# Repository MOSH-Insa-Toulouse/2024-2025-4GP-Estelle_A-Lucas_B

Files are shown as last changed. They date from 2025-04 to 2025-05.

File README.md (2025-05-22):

# 2024-2025-4GP-Estelle AUBRY-Lucas BOURDARIE
Projet capteur 2024 - 2025 | Estelle AUBRY et Lucas BOURDARIE | 4ème année, 59ème promotion

# Table des matières

[Présentation du projet](https://github.com/MOSH-Insa-Toulouse/2024-2025-4GP-Haistelle-Lucbourd?tab=readme-ov-file#pr%C3%A9sentation-du-projet)

[I - Un capteur à base de graphite, c'est possible ?](https://github.com/MOSH-Insa-Toulouse/2024-2025-4GP-Haistelle-Lucbourd?tab=readme-ov-file#i---un-capteur-%C3%A0-base-de-graphite-cest-possible-)

[II - Simulation sous LTSpice](https://github.com/MOSH-Insa-Toulouse/2024-2025-4GP-Haistelle-Lucbourd?tab=readme-ov-file#ii---simulation-sous-ltspice)

[III - Réalisation du PCB avec KiCAD](https://github.com/MOSH-Insa-Toulouse/2024-2025-4GP-Haistelle-Lucbourd?tab=readme-ov-file#iii---r%C3%A9alisation-du-pcb-avec-kicad)

[IV - Le banc de test automatisé](https://github.com/MOSH-Insa-Toulouse/2024-2025-4GP-Haistelle-Lucbourd?tab=readme-ov-file#iv---le-banc-de-test-automatis%C3%A9)

[V - Le code Arduino pour piloter le projet](https://github.com/MOSH-Insa-Toulouse/2024-2025-4GP-Haistelle-Lucbourd/tree/main?tab=readme-ov-file#v---le-code-arduino-pour-piloter-le-projet)

[VI - L'application Android avec Mit App Inventor](https://github.com/MOSH-Insa-Toulouse/2024-2025-4GP-Haistelle-Lucbourd/tree/main?tab=readme-ov-file#vi---lapplication-android-avec-mit-app-inventor)

[VII - Résultats](https://github.com/MOSH-Insa-Toulouse/2024-2025-4GP-Haistelle-Lucbourd/tree/main?tab=readme-ov-file#vii---résultats)

# Présentation du projet 
 
<div align="justify"> Ce projet a été mené dans le cadre de l'UF  "Du capteur au banc de test" . L'objectif est de réaliser un capteur de déformation à base de graphite. Pour ce faire, il suffit simplement de déposer du crayon à papier sur un bout de feuille. La tension ou la compression du papier engendre une variation de résistance qui est proportionnelle à la déformation appliquée. Les principes physiques qui se cachent derrière ce phénomène sont expliqués <a href="https://github.com/MOSH-Insa-Toulouse/2024-2025-4GP-Haistelle-Lucbourd/blob/main/README.md#i---un-capteur-%C3%A0-base-de-graphite-cest-possible-">ici</a>. Le projet s'inscrit donc dans une démarche low-tech car le capteur nécessite peu de ressources et sa réalisation est accessible à tous !</div>

<div align="justify"> De plus, le capteur graphite réalisé sera testé de manière à comparer ses performances avec un capteur de déformation commercial. Nous souhaitons dégager les forces et les limites du capteur graphite par rapport à un capteur commercial. Finalement, nous établirons une conclusion quant à la possible industrialisation de ce type de capteur.</div>

<br>

<div style='display:flex' align="center">
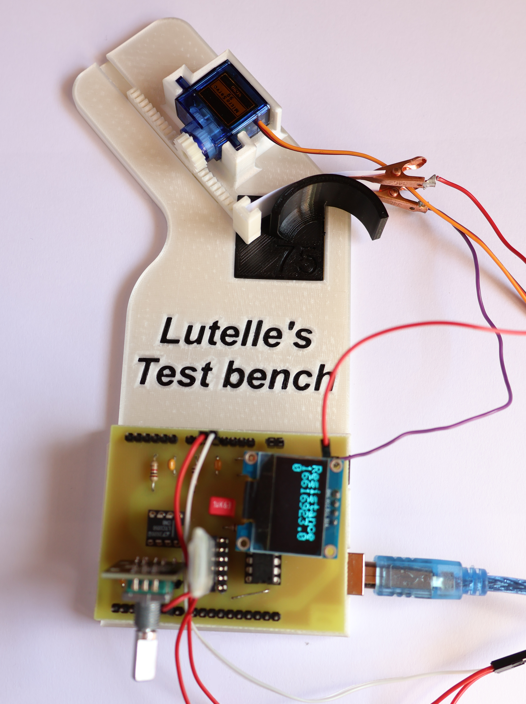
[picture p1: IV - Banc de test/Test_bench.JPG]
   
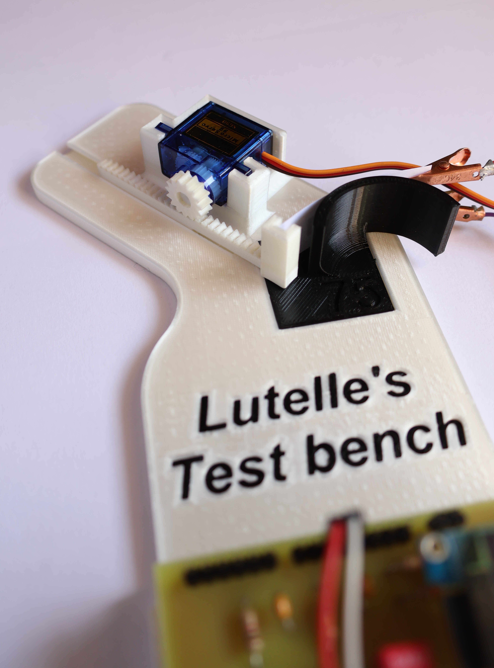
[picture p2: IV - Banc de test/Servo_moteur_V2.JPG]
   
 <p><em>Figure 1 : Banc de test complet </em></p>
</div>

<div style='display:flex' align="center">
   
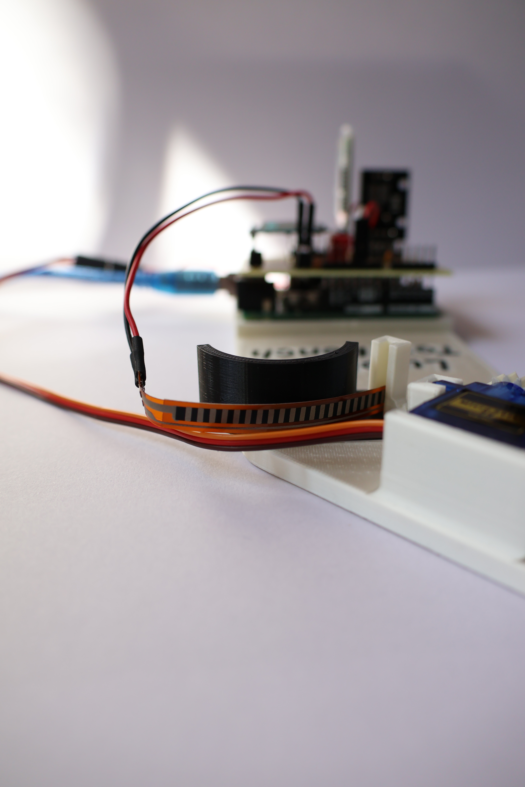
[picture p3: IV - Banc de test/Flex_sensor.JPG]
   
 <p><em>Figure 2 : Mise en place des deux types de capteurs disponibles </em></p>
</div>

 ## Livrables
À la fin de ce projet, plusieurs livrables sont attendus:
- Un **PCB** sur lequel seront connectés tous les éléments cités dans la partie [Matériel utilisé](https://github.com/MOSH-Insa-Toulouse/2024-2025-4GP-Haistelle-Lucbourd/blob/main/README.md#mat%C3%A9riel-utilis%C3%A9)
- Un **banc de test** pour étudier la déformation du capteur graphite et du capteur commercial
- Un **code Arduino** qui permette de contrôler le banc de test et d'afficher les mesures de résistances
- Une <a href="https://github.com/MOSH-Insa-Toulouse/2024-2025-4GP-Haistelle-Lucbourd/blob/main/LSG180_datasheet.pdf"><strong>datasheet</strong></a> qui énonce toutes les caractéristiques du capteur graphite
- Une **application Android** (.apk) pour visualiser les relevés de mesures en direct

## Matériel utilisé 
Pour le **montage**, voici tout le matériel requis:
- Une carte Arduino UNO
- Un écran OLED (I2C) 
- Un module Bluetooth HC-05
- Un potentiomètre numérique MCP41050
- Un encodeur rotatif
- Un capteur de déformation commercial (FlexSensor) pour effectuer une comparaison
- Un <a href="https://github.com/MOSH-Insa-Toulouse/2024-2025-4GP-Haistelle-Lucbourd/blob/main/Jauge_Contrainte_A_Imprimer.pdf"><strong>capteur de déformation en papier</strong></a>
- Des crayons à papiers différents pour les tests
- Un servo moteur
- Des header de différentes tailles pour fixer les composants sur la PCB
- Une résistance de 33k

Pour réaliser **l'amplificateur transimpédance**, la liste de matériel est la suivante:
- Un amplificateur opérationnel LTC1050
- Deux condensateurs de 100nF
- Un condensateur de 1uF
- Deux résistances de 100k
- Deux résistances de 1k
- Une résistance de 10k

# I - Un capteur à base de graphite, c'est possible ?

<div align="justify">
Oui et c'est ce qu'a montré l'équipe de chercheurs Lin, CW., Zhao, Z., Kim, J. et al. dans l'article <em>Pencil Drawn Strain Gauges and Chemiresistors on Paper</em> paru en 2014. En effet, les crayons à papier sont composés de graphite et d'argile dans des proportions différentes. Par exemple, le crayon HB est constitué à 50% de graphite et à 50% d'argile. Ces différences de compositions entraînent des propriétés de conduction qui diffèrent selon le type de crayon utilisé. Lorsque l'on dépose du crayon à papier sur une feuille, les nanoparticules de graphite déposées constituent un système dit <strong>granulaire</strong>. Il s'agit d'un système dont les grains forment un réseau très désordonné au sein duquel les électrons se déplacent d'un grain à un autre par <strong>effet tunnel</strong>. L'équipe de chercheurs a donc démontré que les crayons <strong>durs</strong> comme l'HB possédaient une résistance plus importante que les crayons <strong>légers</strong> comme le 9B. Ceci s'explique par le fait que les crayons durs comme l'HB contiennent plus d'argile qu'un crayon léger qui contient plus de graphite. L'argile joue le rôle d'un isolant, plus il y en a, plus la conduction des électrons au sein du matériau est difficile. À l'inverse, les nanoparticules de graphite permettent la conduction des électrons, c'est pour cela que le crayon 9B est moins résistif que le crayon HB. 
</div>
 <br>
<div align="center">
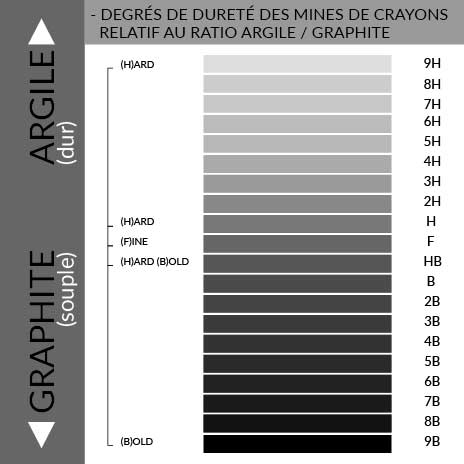
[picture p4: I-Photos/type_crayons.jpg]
  
  <p><em>Figure 3 : Les différents types de crayons: du 9B au 9H</em></p>
 <p><em>d'après le site Passage Clouté à l'adresse<a href="https://passagecloute.com/blog/post/8_comment-choisir-le-bon-crayon-graphite-du-9h-au-9b.html?page_type=post"> suivante</a> </em></p>
</div>
<div align="justify">
De plus, les chercheurs ont aussi prouvé que les crayons pouvaient se comporter comme des <strong>jauges de contraintes</strong>. En dessinant au crayon une forme de U avec deux rectangles au bout pour les électrodes de contact, les chercheurs ont remarqué qu'une déformation en compression et en tension avaient des effets différents sur la <strong>résistance</strong> du capteur. La compression du capteur compresse les particules de graphite et induit une diminution de la résistance. Au contraire, la tension du capteur éloigne les particules de graphite ce qui augmente résistance. 
</div>
<div align="center">
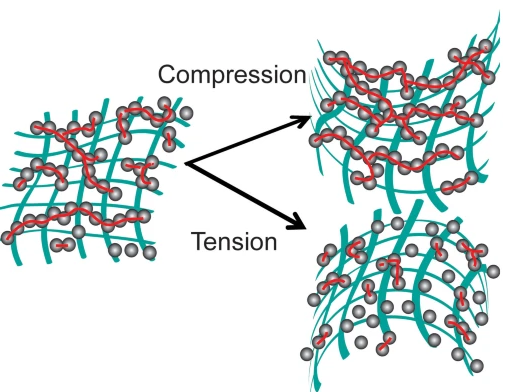
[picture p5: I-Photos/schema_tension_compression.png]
  
  <p><em>Figure 4 : Structure granulaire en compression et en tension</em></p>
</div>

<div align="center">
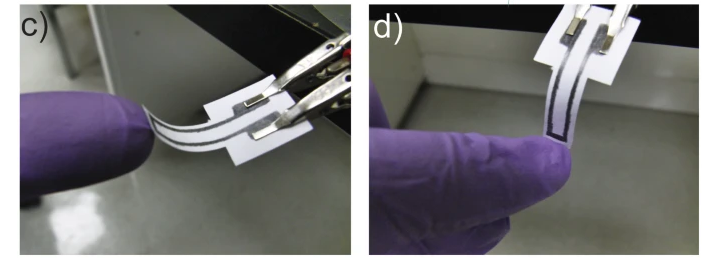
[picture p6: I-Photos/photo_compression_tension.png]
  
  <p><em>Figure 5 : c) Capteur graphite en compression d) Capteur graphite en tension </em></p>
 <p><em>d'après Lin, CW., Zhao, Z., Kim, J. et al., 2014 </em></p>
</div>

<div align="justify">
Cependant, l'équipe conclut que l'observation de ces phénomènes n'est pas possible pour des crayons composés de plus d'argile que le crayon HB. Selon eux, le réseau de nanoparticules du crayon HB se situe juste au dessus du <strong>seuil de percolation</strong>. Le seuil de percolation est le seuil à partir duquel le matériau devient conducteur car les électrons peuvent traverser. Néanmoins, nous allons montrer que, grâce à l'utilisation d'un <strong>amplificateur transimpédance</strong>, il est possible de mesurer des résistances pour des crayons plus durs que le HB. Par conséquent, la structure de ces crayons permet le passage des électrons et ne se situe pas en dessous du seuil de percolation.   
</div>

# II - Simulation sous LTSpice et formules utiles

<div align="justify"> D'après l'étude menée par les chercheurs, le capteur graphite a une résistance qui peut varier d'une centaine de kohms à quelques Mohms. Les résistances très élevées sont délicates à mesurer. En effet, une méthode classique consiste à utiliser un ohmmètre mais pour mesurer des résistances de cet ordre de grandeur les options sont chères. De plus, nous utilisons une carte Arduino dont l'impédance maximale de la source ne peut pas dépasser 10 kohms. Il n'est donc pas possible de brancher directement notre capteur graphite sur la carte. De ce fait, nous allons amplifier le signal et diminuer son impédance à l'aide d'un amplificateur transimpédance. Nous utilisons pour cela un amplificateur opérationnel LTC1050 car il est suffisamment sensible pour amplifier correctement le signal. Il s'agit également d'un amplificateur très précis, qui possède un offset voltage de 5 uV, négligeable par rapport à la tension mesurée sur l'entrée non-inverseuse. Si l'on considère que le courant délivré par le capteur graphite est de 100 nA et que la résistance de R1 vaut 100komhs, alors la tension Vep = I x R1 = 10 mV >> 5 uV.</div>

## A) Montage avec l'amplificateur transimpédance

<div align="center">
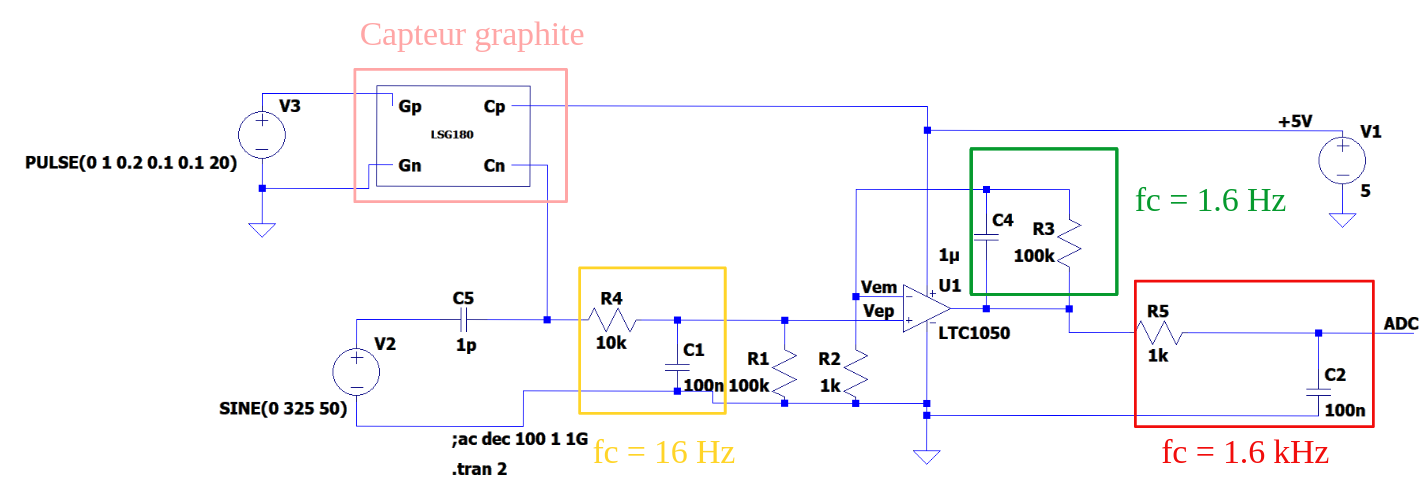
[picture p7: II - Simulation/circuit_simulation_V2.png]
  
  <p><em>Figure 6 : Schéma de l'amplificateur transimpédance dans LTSpice </em></p>
</div>
<div align="justify">
De plus, il va falloir filtrer le bruit. Pour ce faire, nous mettons en place 3 filtres passe-bas:
 <ul>
  <li>un pour filtrer le bruit du capteur en jaune.</li>
  <li>un pour filtrer le bruit à 50Hz en vert.</li>
  <li>un pour filtrer les variations plus rapides que 7kHz en rouge. D'après le critère de Shannon, fech > 2*fsignal. Or, pour une carte Arduino, la fréquence d'échantillonnage vaut 15 kHz donc fsignal < 7kHz.  </li>
</ul>
</div>

## B) Formules
À partir de ce montage, nous pouvons établir la formule nécessaire pour relier la tension en sortie de l'amplificateur transimpédance à la résistance du capteur graphite.

<div align="center">
  
  <p><em>Equation 1 : Formule qui lie la résistance du capteur graphite à la tension Vadc mesurée en sortie </em></p>
</div>

De la même manière, pour le capteur commercial, nous faisons un pont diviseur de tension avec une résistance de 33k. La formule qui relie la tension de sortie à la résistance du capteur commercial est la suivante: 

<div align="center">
  
  <p><em>Equation 2 : Formule qui lie la résistance du capteur commercial à la tension V_flex mesurée en sortie </em></p>
</div>

# III - Réalisation du PCB avec KiCAD

<div align="justify"> Ensuite, nous avons dessiné un PCB simple face à l'aide du logiciel KiCAD. Il est à noter que l'entrée du capteur graphite est reliée à l'amplificateur transimpédance. Afin de permettre un meilleur contrôle de l'amplification du signal, la résistance R2 de la figure 7 a été remplacée par un potentiomètre numérique. Le conditionneur utilisé pour le capteur commercial est un pont diviseur de tension avec une résistance de 33k. De plus, nous avons ajouté un condensateur pour faire du débouncing sur l'encodeur rotatif. Nous avons suivi ces étapes:</div>

**1)** **Dessiner** les composants tels que l'OLED, l'encodeur rotatif, le module Bluetooth, le capteur commercial et le capteur graphite

**2)** Réaliser les **empreintes** de ces composants

**3)** Sélectionner les résistances, les condensateurs et l'AOP pour **réaliser l'amplificateur transimpédance** dans l'éditeur de Schématique

**4)** Établir les **points de connexion** entre la carte Arduino et tous les composants

**5)** **Positionner** les composants sur la PCB

**6)** Importer les **modèles 3D** pour les composants non-présents par défaut dans les librairies (OLED, encoder rotatif, module Bluetooth, capteur commercial)

**7)** Faire **le routage** dans l'éditeur de PCB en évitant au maximum les masses flottantes et les vias

**N.B**: Le servo moteur n'apparaît pas ici car il sera relié à la carte Arduino par le biais d'un header.
<div align="center">
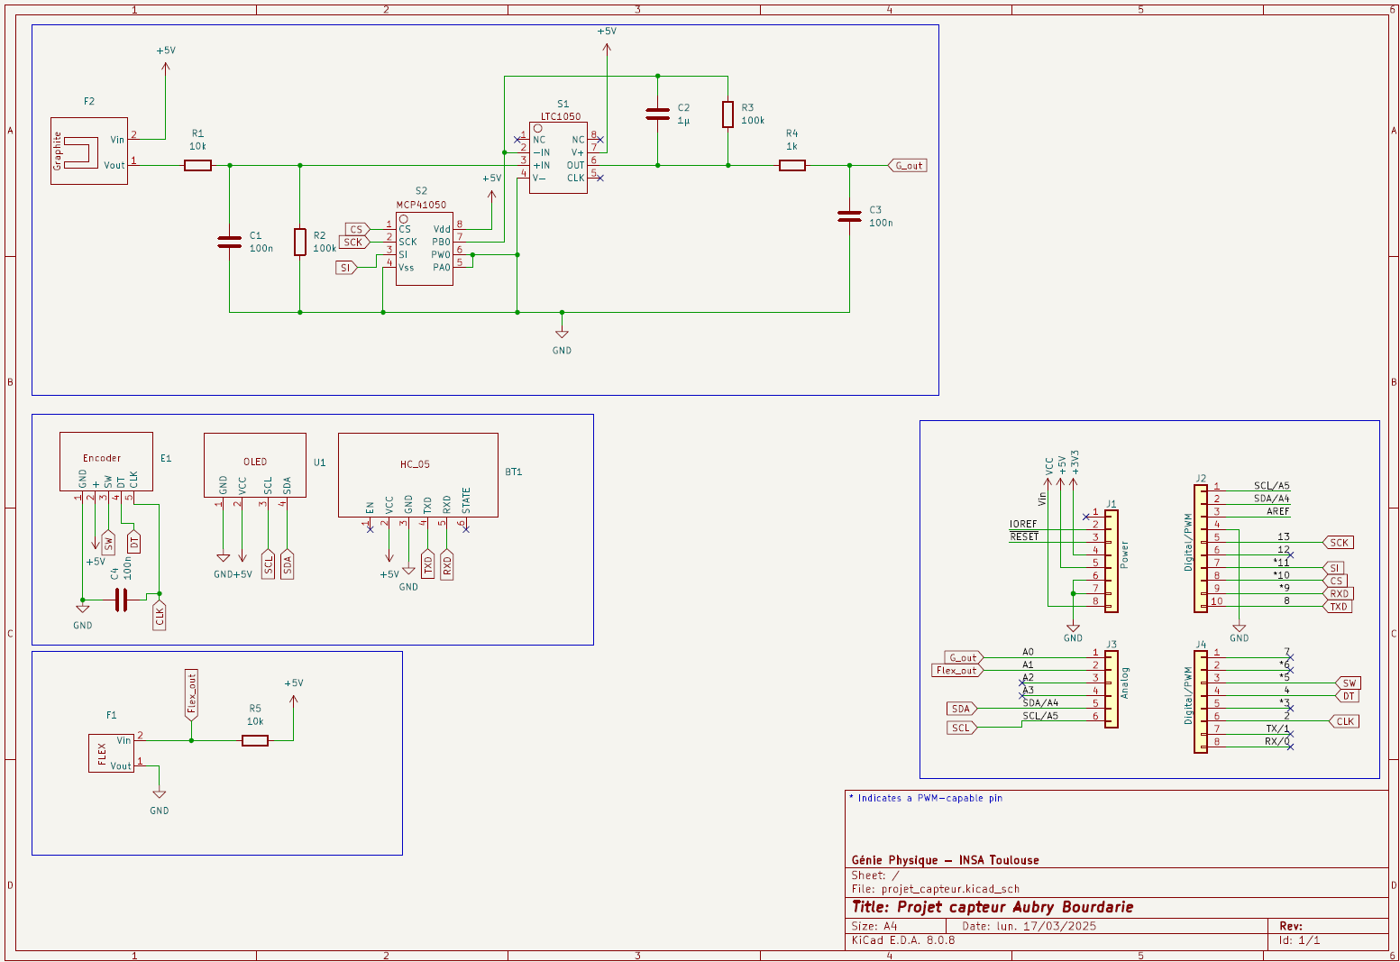
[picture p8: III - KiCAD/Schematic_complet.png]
  
  <p><em>Figure 7 : Vue depuis l'éditeur de Schématique </em></p>
</div>

<div align="center">
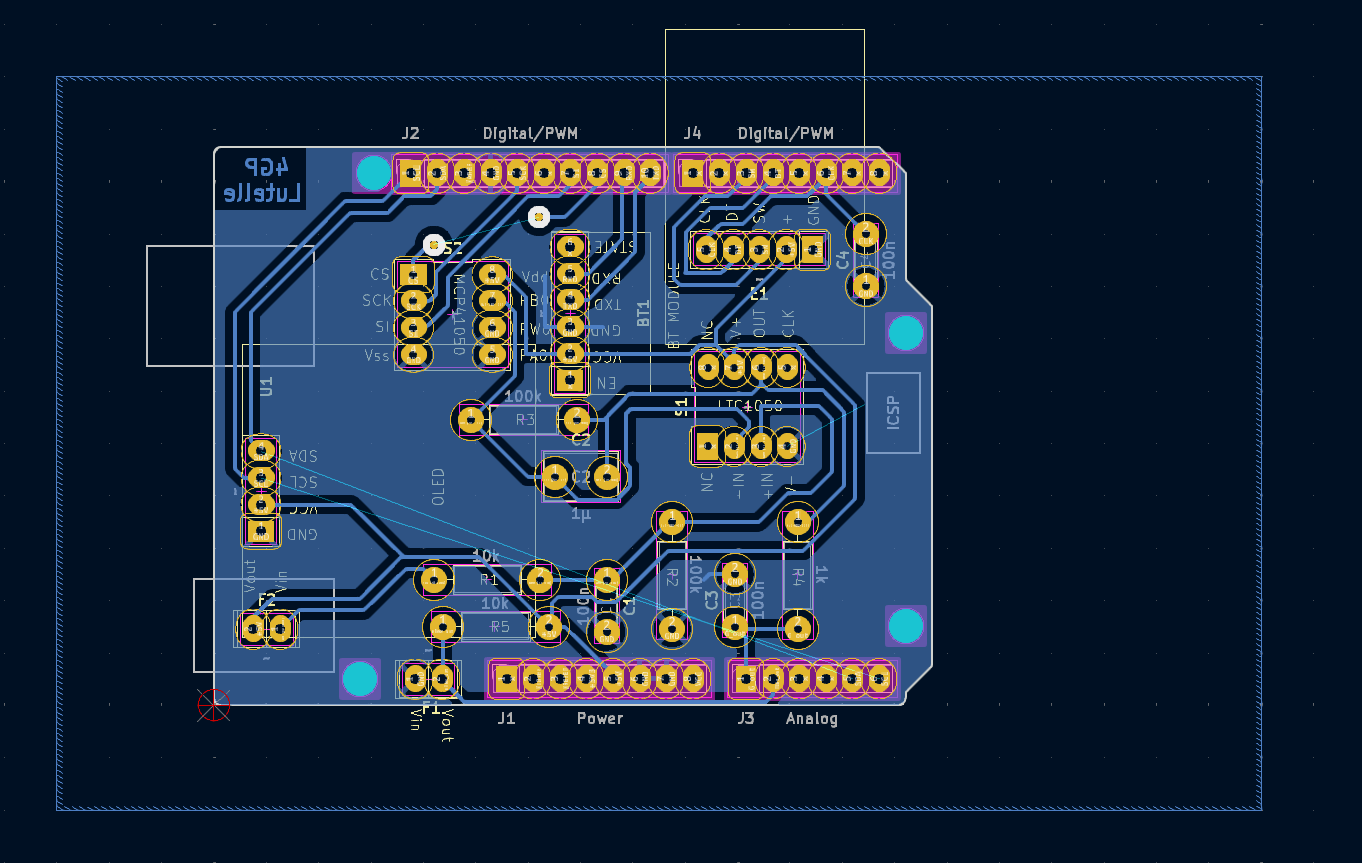
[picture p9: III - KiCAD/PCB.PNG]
  
  <p><em>Figure 8 : Vue depuis l'éditeur de PCB </em></p>
</div>

<div align="center">
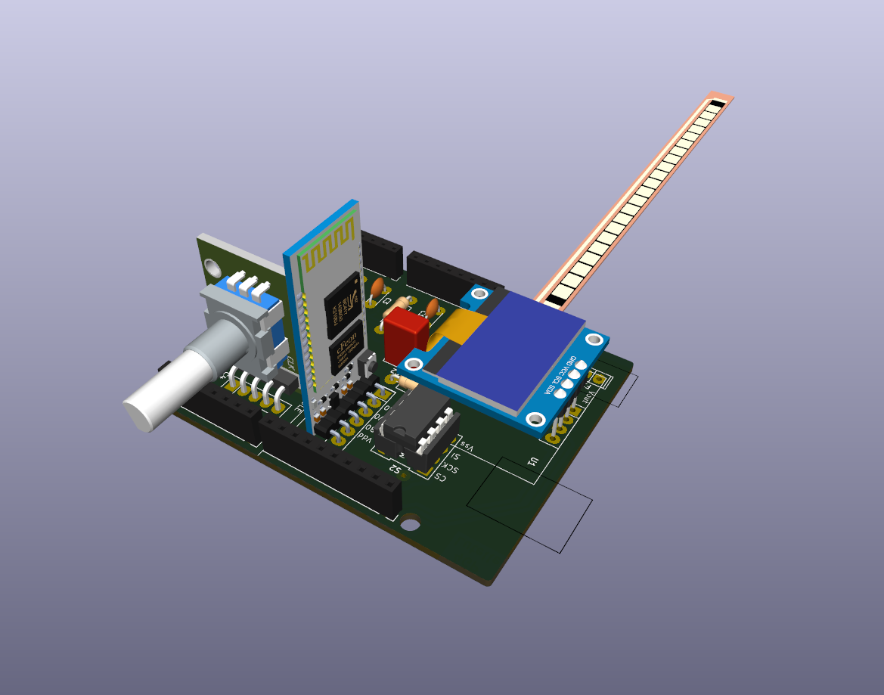
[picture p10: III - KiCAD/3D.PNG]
  
  <p><em>Figure 9 : Vue 3D </em></p>
</div>

# IV - Le banc de test automatisé

<div align="center">
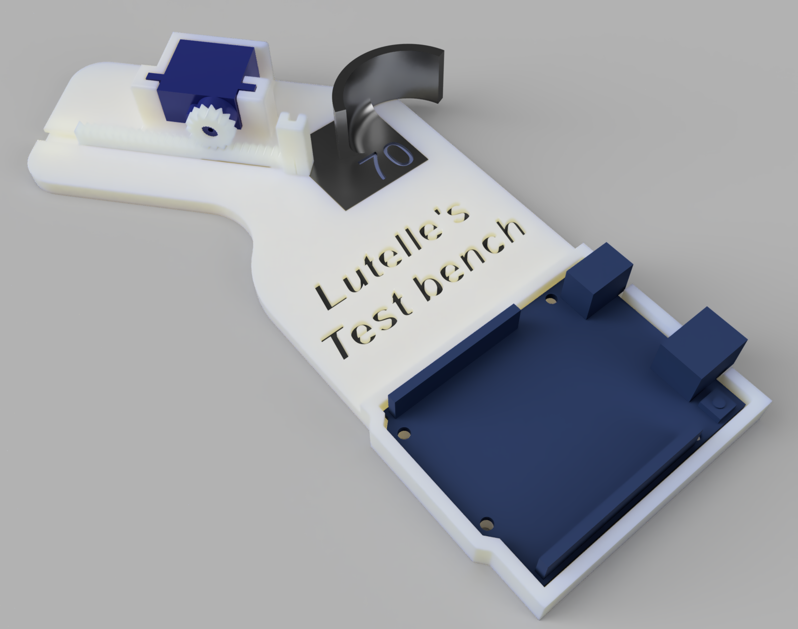
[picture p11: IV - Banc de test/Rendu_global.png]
  
  <p><em>Figure 10 : Rendu du banc de test final</em></p>
</div>

<div align="justify"> Afin d'optimiser notre relevé de mesures, nous avons mis au point un banc de test qui courbe automatiquement le capteur de déformation. De cette manière, nous minimisons les risques de dégradation du capteur graphite lors des relevés de mesure car nous ne touchons pas le capteur dès lors qu'il est positionné sur le banc de test. Le banc de test a été réalisé sous Fusion360 puis imprimé en 3D. Ce dernier permet des relevés entièrement personnalisables par l'utilisateur grâce au code Arduino développé. Avec ce banc de test, il est possible de réaliser des mesures sur le capteur graphite et le capteur commercial. Les mesures en tension se sont révélées être plus faciles à mettre en place que les mesures en compression, qui sont plus délicates.</div>

## A) La glissière pilotée par le servo moteur

<div align="center">
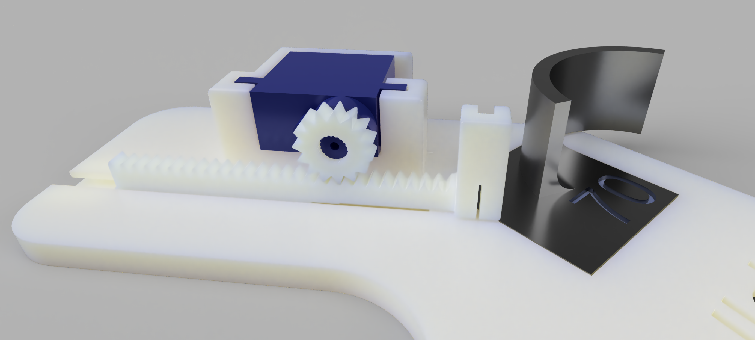
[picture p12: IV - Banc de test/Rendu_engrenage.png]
  
  <p><em>Figure 11 : Rendu de la glissière écrantée avec encoche fendue ainsi que de l'engrenage fixé au servo</em></p>
</div>

<div align="justify">  Pour courber le capteur de déformation, nous avons utilisé un système de glissière qui se déplace sous l'action du servo moteur. En effet, nous avons conçu un engrenage qui se fixe sur le servo moteur et dont la rotation entraîne une glissière crantée. Le bout de cette glissière est fait en forme d'encoche pour maintenir le capteur. Pour éviter que le capteur sorte de l'encoche au cours des mesures, nous avons également imprimé des petites cales qui assurent le bon positionnement du capteur. Enfin, nous avons imprimé deux glissières différentes, une pour le capteur commercial et une pour le capteur graphite car le capteur commercial est plus long que le capteur graphite. La glissière du capteur commercial possède une petite fente en bas de l'encoche (voir figure 11) pour le maintenir correctement et permettre une déformation qui épouse au mieux les rayons de courbure.</div>

## B) Les rayons de courbure interchangeables
<div style='display:flex' align="center">
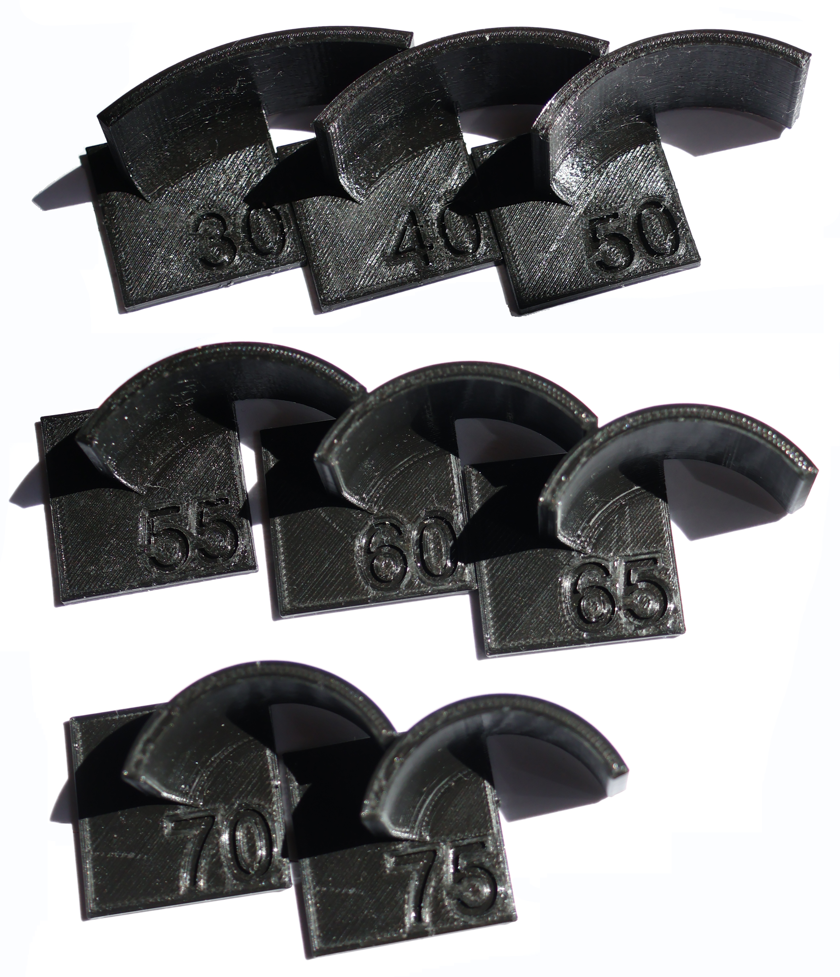
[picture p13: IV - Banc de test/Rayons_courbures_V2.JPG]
   
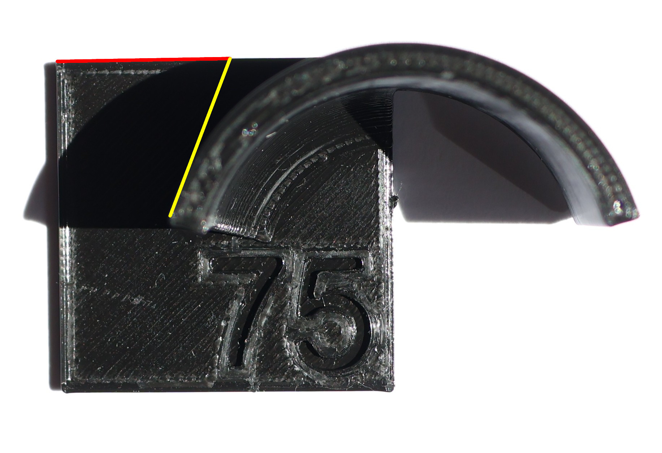
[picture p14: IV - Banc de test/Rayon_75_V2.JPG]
   
 <p><em>Figure 12 : Gamme de rayons de courbure imprimés en 3D</em></p>
</div>

<div align="justify"> Pour tester les capteurs, nous avons imprimé huit supports en 3D avec différents rayons de courbure. Ces supports s'imbriquent sur le banc de test comme nous pouvons le voir sur la figure 11. Les numéros qui figurent sur les supports correspondent à l'angle entre le bord jaune et le bord rouge indiqués sur la figure 12. 
</div>

# V - Le code Arduino pour piloter le projet

## A) Description générale 

<div align="justify"> Le code développé permet à l'utilisateur de gérer facilement et intuitivement le banc de test pour effectuer les mesures. L'affichage se fait sur l'écran OLED sur lequel apparaissent <a href="https://github.com/MOSH-Insa-Toulouse/2024-2025-4GP-Haistelle-Lucbourd/tree/main?tab=readme-ov-file#b-les-diff%C3%A9rentes-fonctionalit%C3%A9s">les différentes fonctionnalités</a>. L'utilisateur peut parcourir les différents menus en tournant l'encoder rotatif dans le sens horaire ou anti-horaire. Pour "rentrer" dans un menu, il suffit d'appuyer sur l'encoder et l'interface se met à jour. Chaque menu possède sa propre fonctionnalité que l'utilisateur peut librement régler. En principe, l'ordre des menus correspond à l'ordre dans lequel l'utilisateur doit effectuer les réglages avant de lancer la mesure via le menu "Démarrage" à la fin. Il est préférable de ne pas placer le capteur sur le banc de test avant le menu "Borne" pour ne pas l'abîmer lors des précédents réglages.</div>

## B) Les différentes fonctionnalités
### 1 - Le menu "BIENVENUE"
<div align="center">
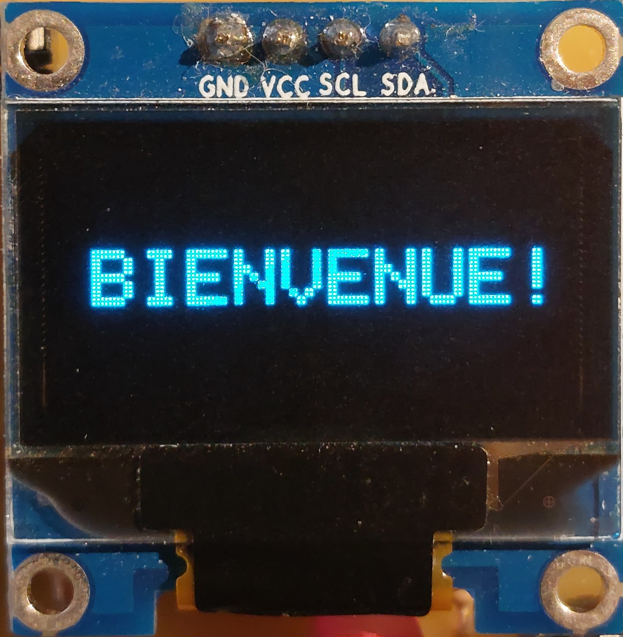
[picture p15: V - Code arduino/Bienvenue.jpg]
   
 <p><em>Figure 13 : menu de bienvenue </em></p>
</div>
Ce menu souhaite la bienvenue à l'utilisateur. Il ne possède pas de fonctionnalité particulière.

### 2 - Le menu "CONFIGURATION"
<div style='display:flex' align="center">
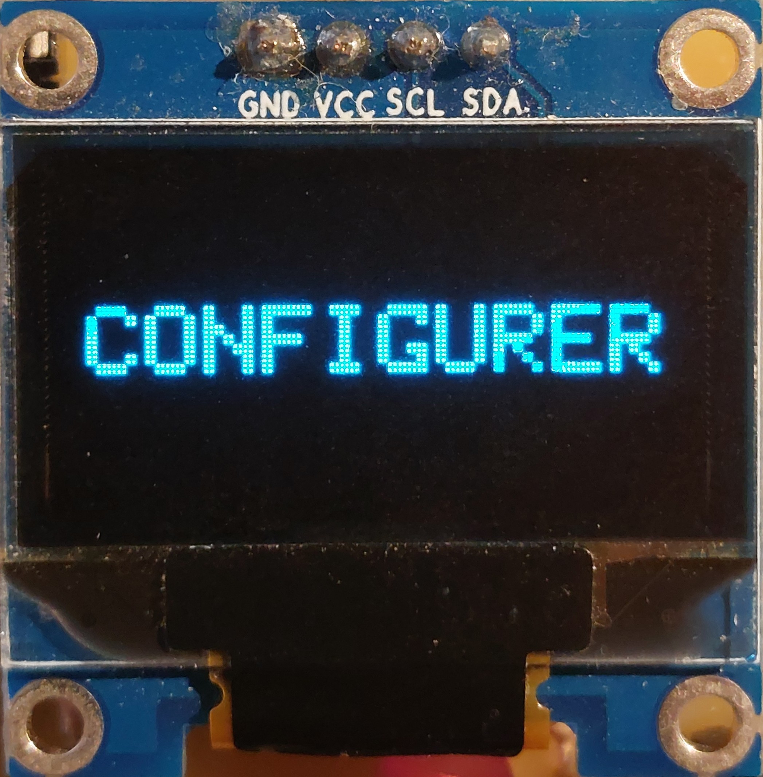
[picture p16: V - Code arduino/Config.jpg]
   
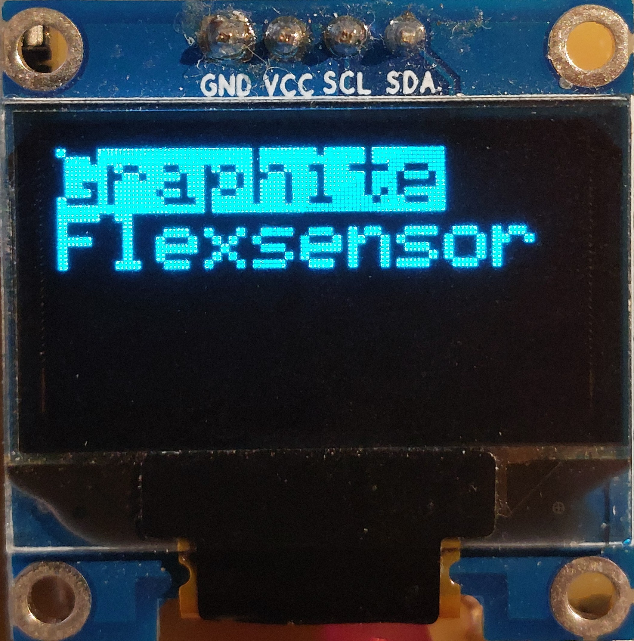
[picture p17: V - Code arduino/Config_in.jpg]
   
 <p><em>Figure 14 : menu de configuration </em></p>
</div>
<div align="justify"> Ce menu permet à l'utilisateur de définir quel type de capteur il utilise entre le capteur graphite et le capteur commercial. Une fois le type de capteur sélectionné (fond bleu et écriture noire), il suffit d'appuyer sur l'encoder rotatif pour enregistrer le choix. </div>

### 3 - Le menu "CALIBRATION"
 <div style='display:flex' align="center">
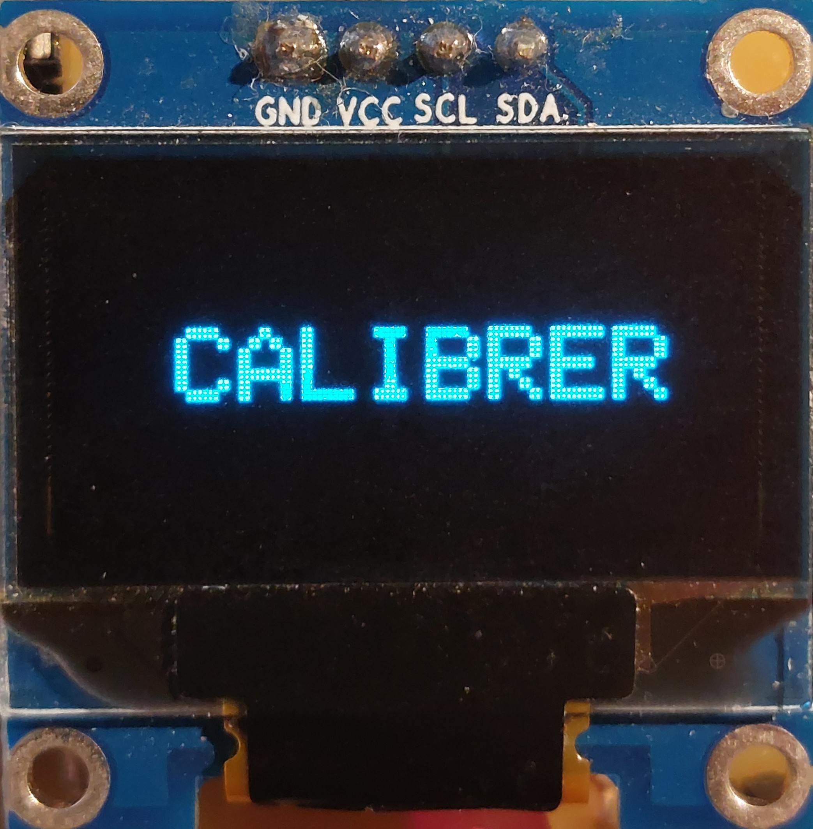
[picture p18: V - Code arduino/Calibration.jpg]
   
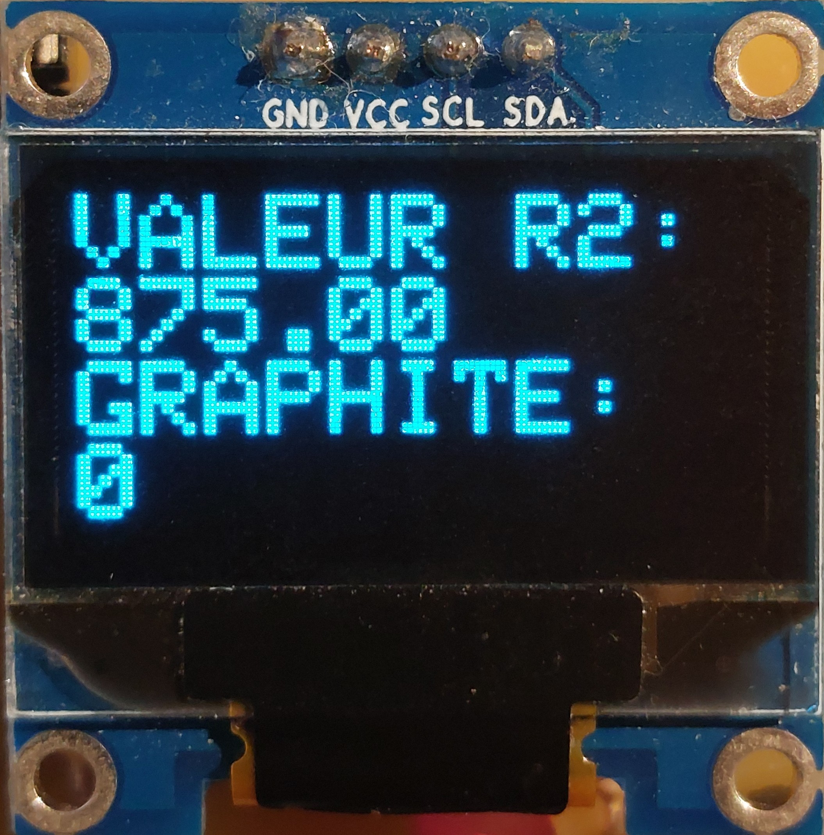
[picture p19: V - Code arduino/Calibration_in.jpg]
   
 <p><em>Figure 15 : menu de calibration </em></p>
</div>
<div align="justify"> Dans ce menu, l'utilisateur peut régler la valeur prise par le potentiomètre numérique de manière à ne pas saturer l'amplificateur opérationnel. Attention, ce menu n'est utile que lorsque le type de capteur choisi est le graphite car le potentiomètre numérique est utilisé dans l'amplificateur transimpédance. L'interface affiche à la fois la valeur de résistance prise par le potentiomètre numérique et le signal lu par l'entrée analogique du capteur graphite. Il s'agit donc d'une valeur comprise entre 0 et 1023. Lors des mesures, il faut également anticiper la variation de résistance engendrée par la déformation du capteur graphite. En effet, en compression, la résistance lue diminue donc le signal augmente et peut, si le potentiomètre n'est pas correctement réglé, saturer l'AOP. </div>

### 4 - Le menu "VITESSE"
<div style='display:flex' align="center">
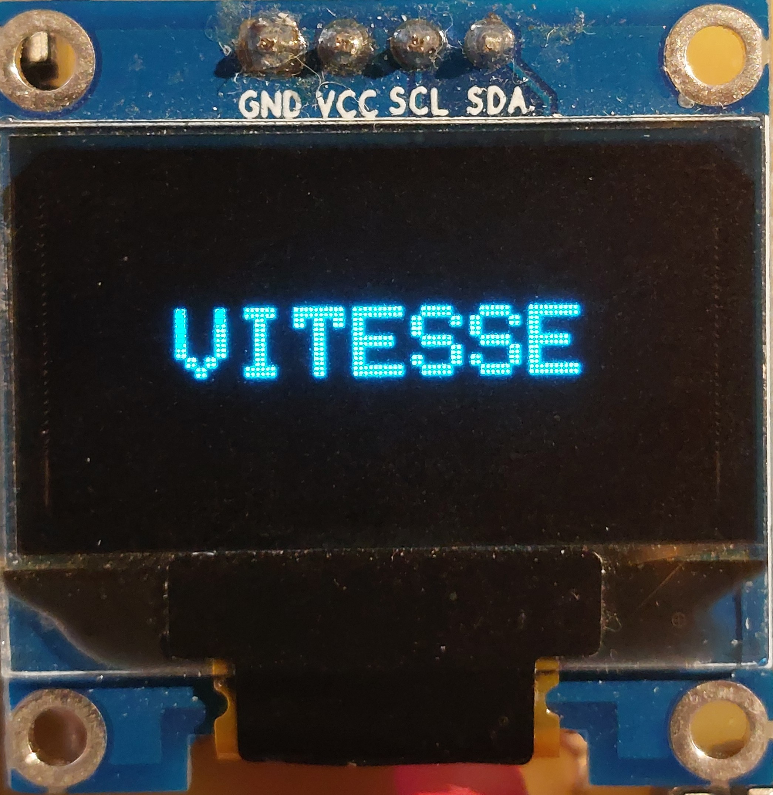
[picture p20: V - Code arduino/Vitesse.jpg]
   
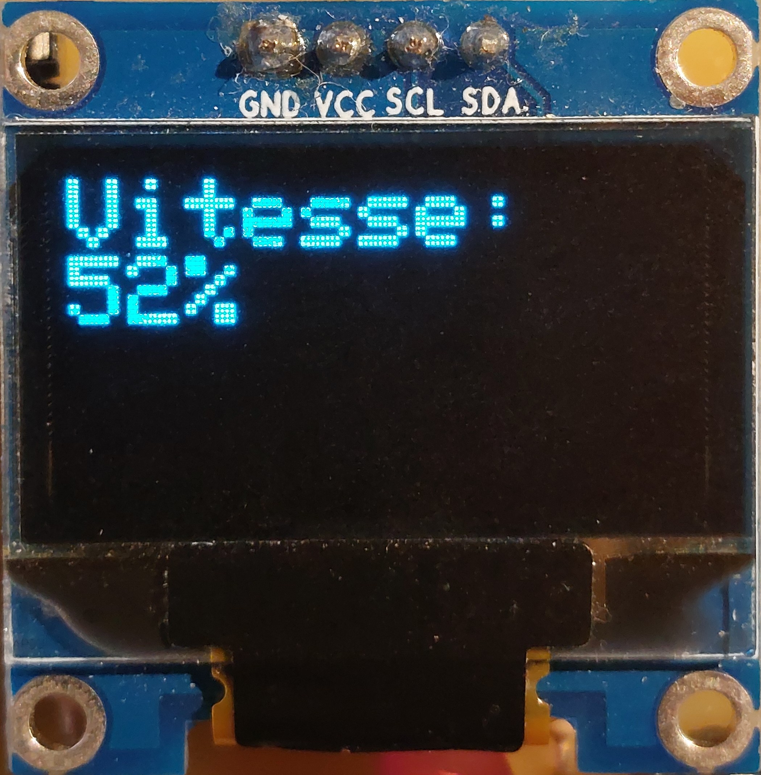
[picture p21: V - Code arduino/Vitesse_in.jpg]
   
 <p><em>Figure 16 : menu de réglage de la vitesse </em></p>
</div>
<div align="justify"> Dans le menu "Vitesse", l'utilisateur peut régler la vitesse à laquelle il souhaite effectuer les mesures, c'est-à-dire, la vitesse à laquelle la glissière reliée au servo moteur va se déplacer. L'écran affiche un pourcentage qui correspond à la vitesse du servo moteur. 0% correspond à la <strong>vitesse minimale</strong> et 100% la <strong>vitesse maximale</strong>. Pour augmenter la vitesse, il est nécessaire de tourner l'encodeur rotatif dans le sens <strong>anti-horaire</strong> car il s'agit en réalité de <strong>diminuer</strong> le délai entre chaque incrément du servo moteur. La vitesse maximale correspond à un délai de <strong>5ms</strong> tandis que la vitesse minimale correspond à un délai de <strong>40ms</strong>. De plus, lorsque la vitesse change (= l'encodeur change de position), le servo moteur effectue un aller-retour au cours duquel il est possible faire varier la vitesse du servo à l'aide de l'encodeur jusqu'à obtenir la vitesse désirée. L'affichage en % de la vitesse s'effectue <strong> à la fin </strong>  de l'aller-retour. Il n'y a donc pas d'affichage en direct de la vitesse mais seulement après que le servo moteur ait fait un aller-retour. D'après la figure 17 ci-dessous, comme l'encodeur est utilisé pour faire varier le délai, la variable encoder_pos peut prendre des valeurs comprises entre 5 et 40 uniquement. </div>
<div align="center">
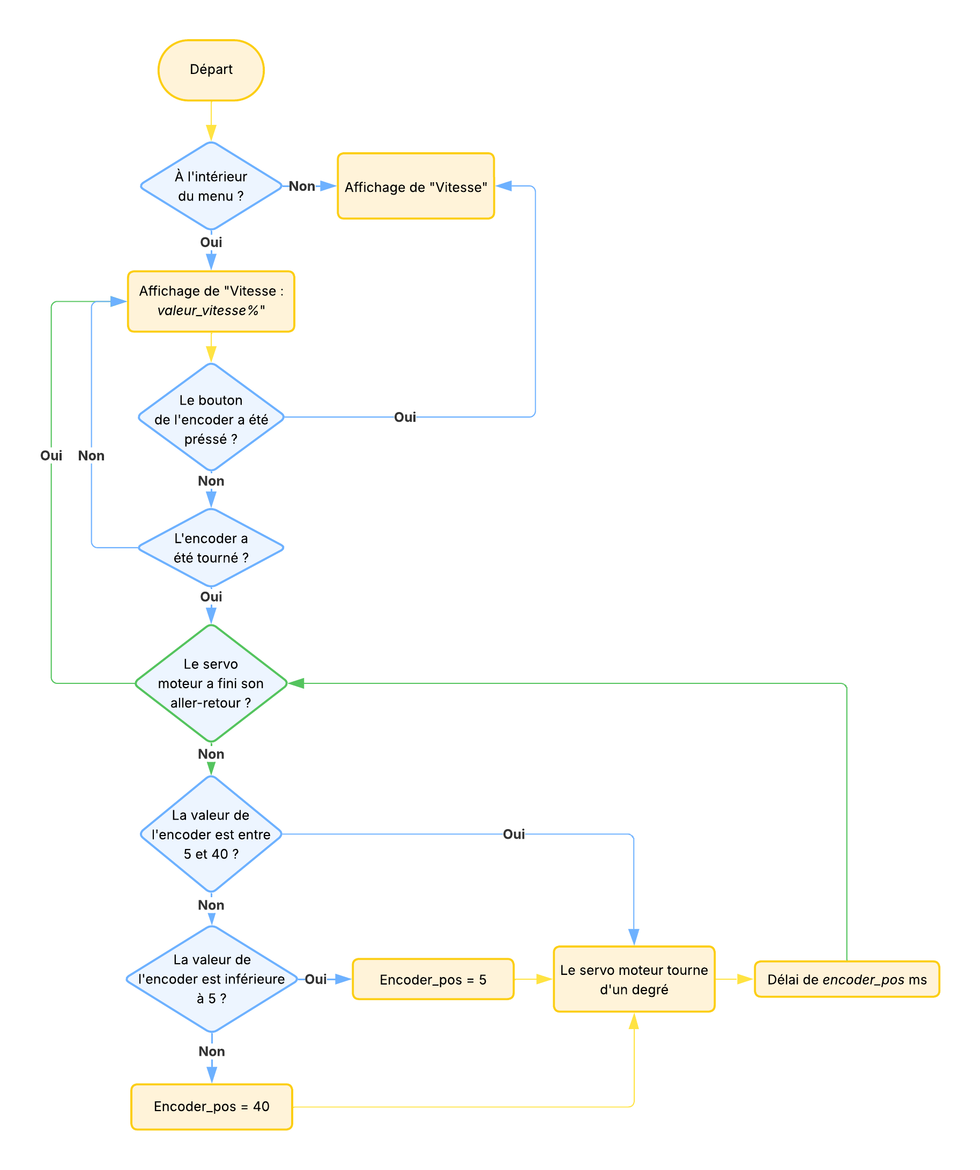
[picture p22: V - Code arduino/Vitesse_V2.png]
  
  <p><em>Figure 17 : Algorigramme qui présente le déroulé de la fonction "Vitesse"</em></p>
</div>

### 5 - Le menu "BORNE"
<div style='display:flex' align="center">
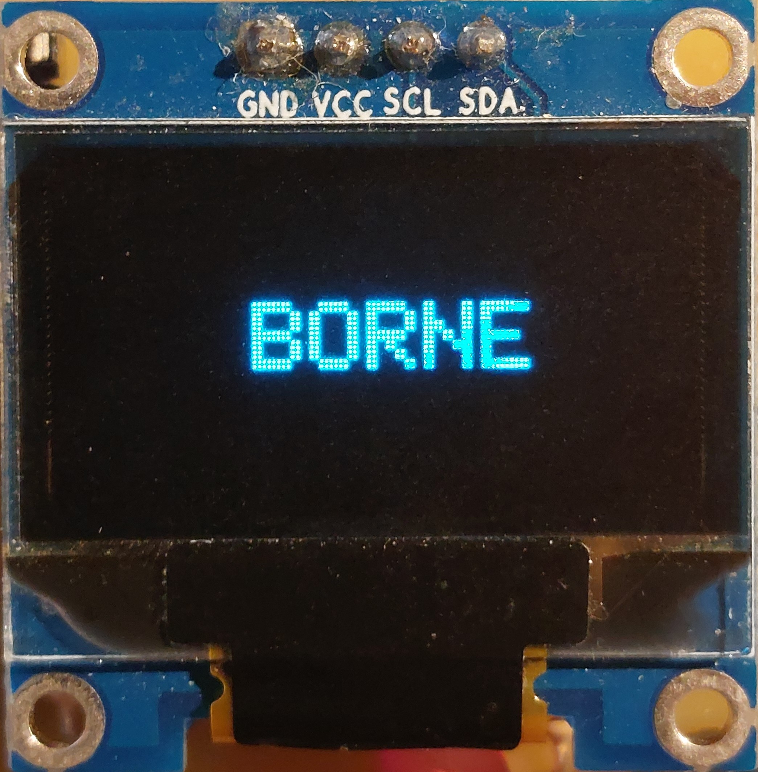
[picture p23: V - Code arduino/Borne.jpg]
   
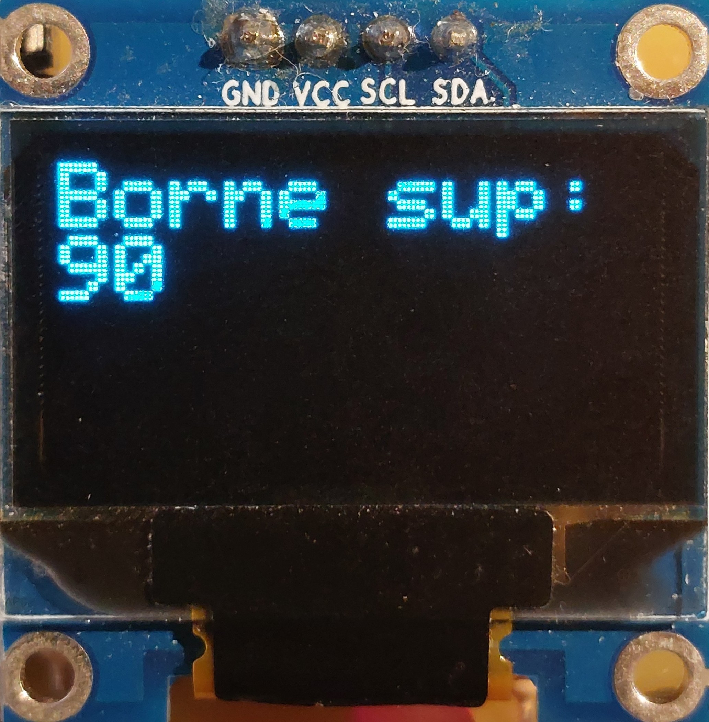
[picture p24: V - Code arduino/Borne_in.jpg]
   
 <p><em>Figure 18 : menu de réglage de la borne </em></p>
</div>
<div align="justify"> À partir de cette étape, il faut placer le capteur sur le banc de test. Le menu "Borne" permet à l'utilisateur de régler la position maximale du servo moteur et par conséquent, celle de l'encoche qui maintient le capteur contre le support. De cette manière, l'utilisateur peut s'assurer que le capteur épouse correctement la forme du rayon de courbure. Pour augmenter ou diminuer la position maximale, il faut tourner l'encodeur rotatif dans le sens horaire ou anti-horaire. </div>
 
### 6 - Le menu "MODE de MESURE"
<div style='display:flex' align="center">
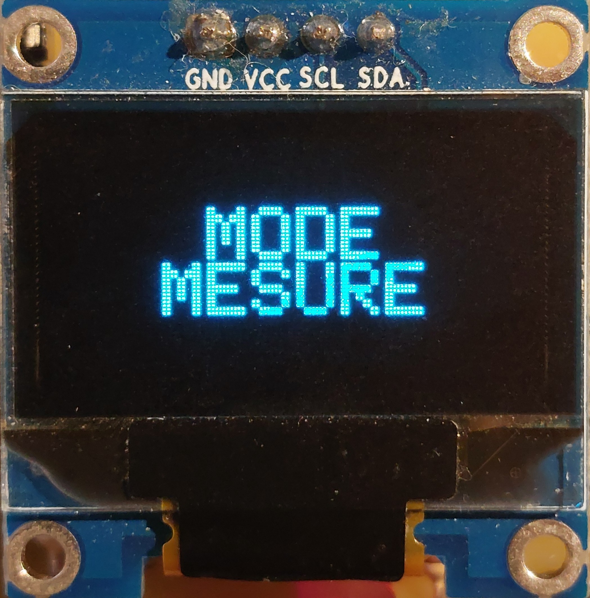
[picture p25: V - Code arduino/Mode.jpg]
   
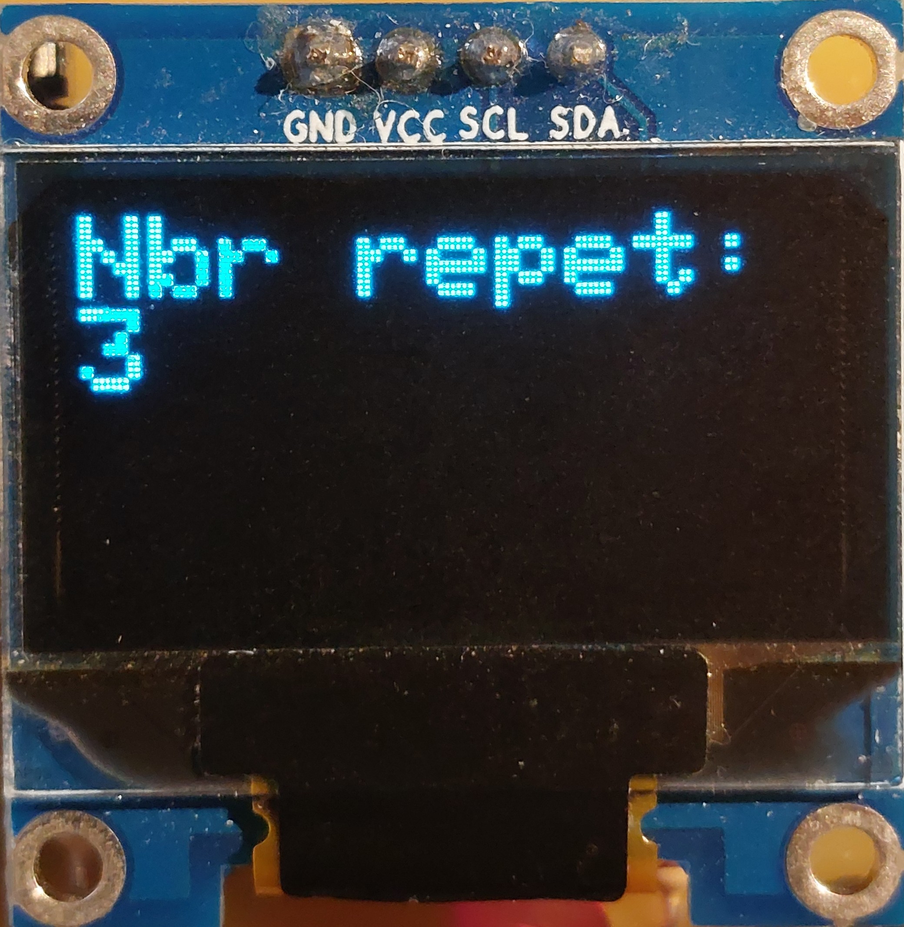
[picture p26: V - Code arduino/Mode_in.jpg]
   
 <p><em>Figure 19 : menu de sélection du mode de mesure </em></p>
</div>
<div align="justify"> À l'intérieur de ce menu, l'utilisateur définit le nombre de mesures qu'il souhaite faire. En effet, nous avons pensé que comme les valeurs de résistances lues en direct peuvent parfois varier, il pourrait être intéressant de permettre à l'utilisateur de faire une moyenne sur un nombre de mesures qu'il définit. De ce fait, lorsque la valeur choisie est "5" par exemple, le code effectuera 5 relevés de résistances pour un même rayon de courbure. Le servo fera donc un aller, une mesure puis un retour, le tout 5 fois. La valeur finale affichée correspondra à une moyenne de la résistance sur les 5 mesures. Le nombre de mesure réalisable est compris entre 1 et 20. </div>

### 7 - Le menu "DÉMARRAGE"
<div style='display:flex' align="center">
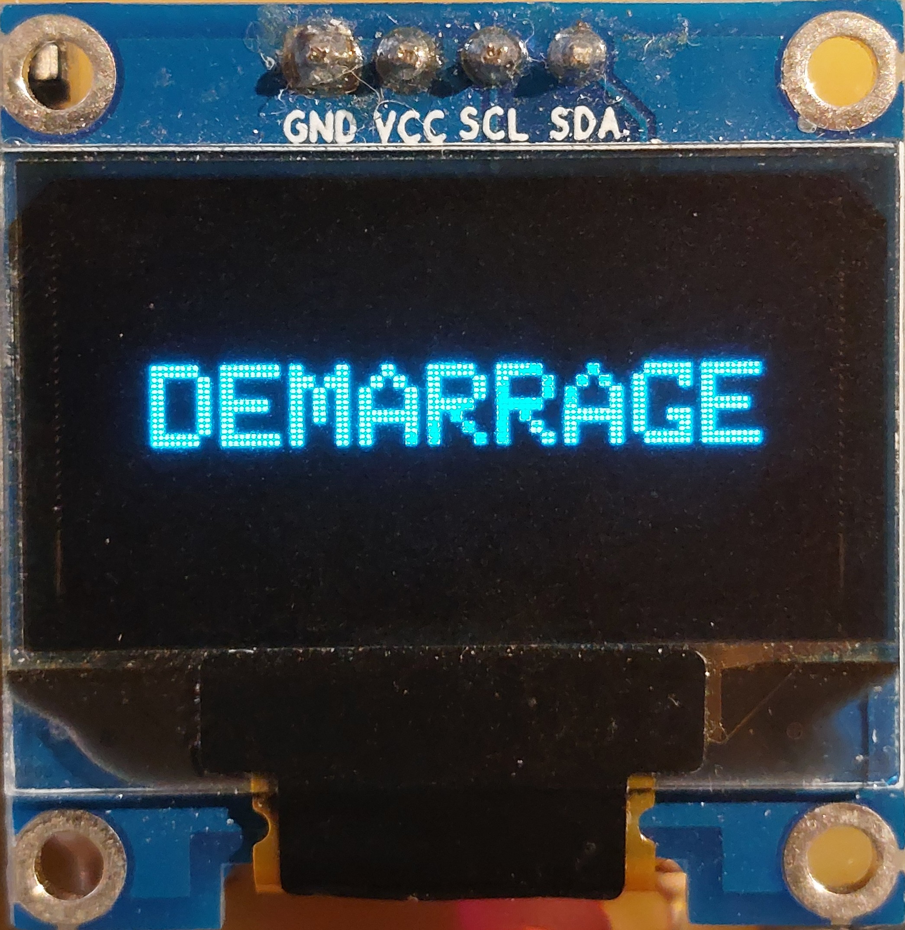
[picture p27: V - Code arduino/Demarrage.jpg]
   
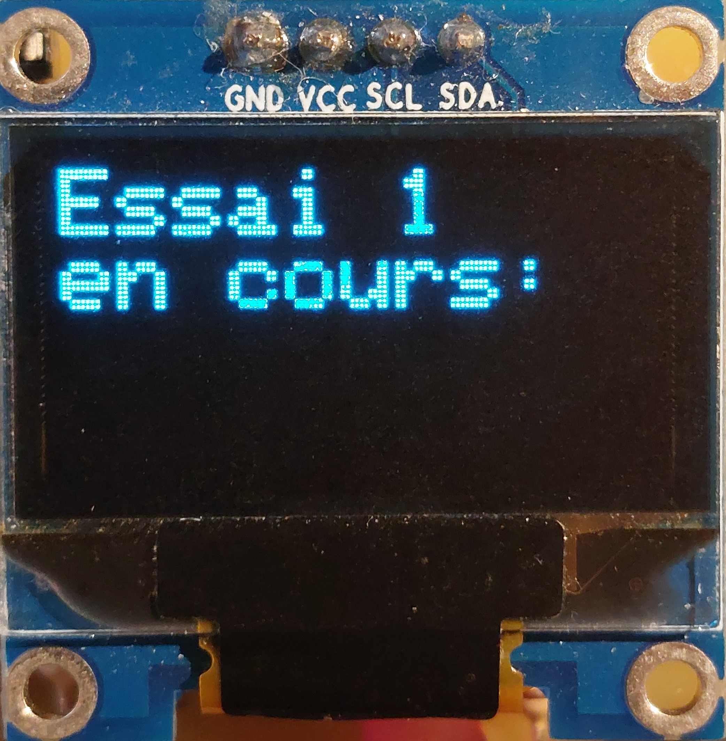
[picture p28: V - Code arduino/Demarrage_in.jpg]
   
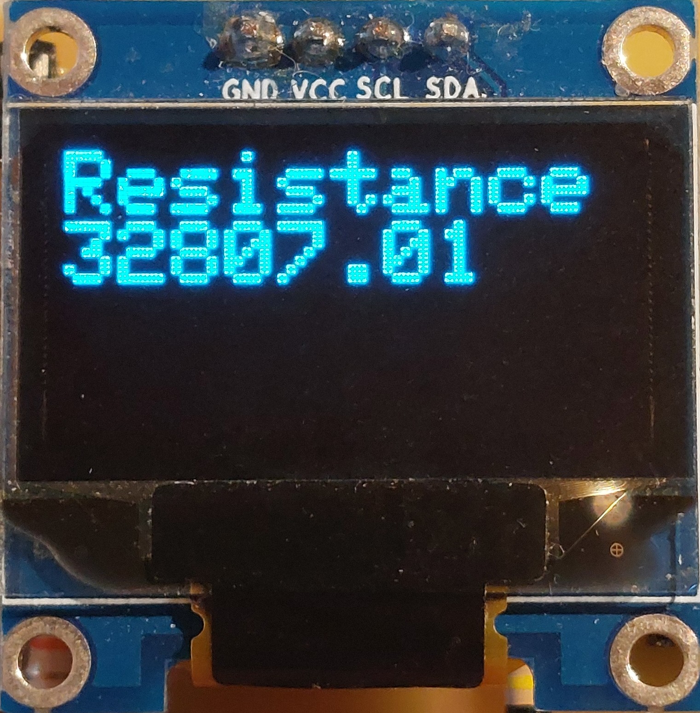
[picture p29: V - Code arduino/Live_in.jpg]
   
 <p><em>Figure 20 : menu de démarrage de la mesure </em></p>
</div>
Le menu "Démarrage" permet de lancer l'acquisition de mesure. Il prend en compte tous les paramètres précédemment définis par l'utilisateur. Par exemple pour des paramètres tels que:
<ul>
<li><strong>Vitesse</strong>: 52%</li>
<li><strong>Borne</strong>: 150</li>
<li><strong>Mode de mesure</strong>: 5</li>
Le servo moteur effectuera 5 aller-retours jusqu'à la position 150 du servo à une vitesse de 52% de la vitesse maximale.
</ul>
<div align="center">
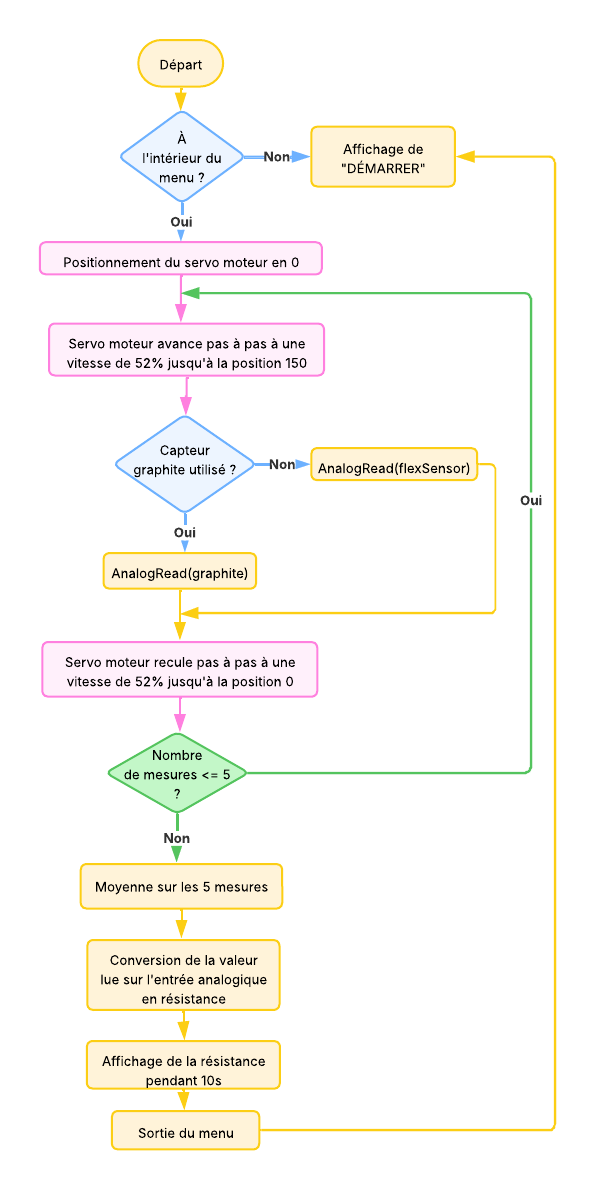
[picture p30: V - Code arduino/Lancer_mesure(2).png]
  
  <p><em>Figure 21 : Algorigramme qui présente le déroulé de la fonction "Démarrage"</em></p>
</div>

### 8 - Le menu "LiveVIEW"
<div style='display:flex' align="center">
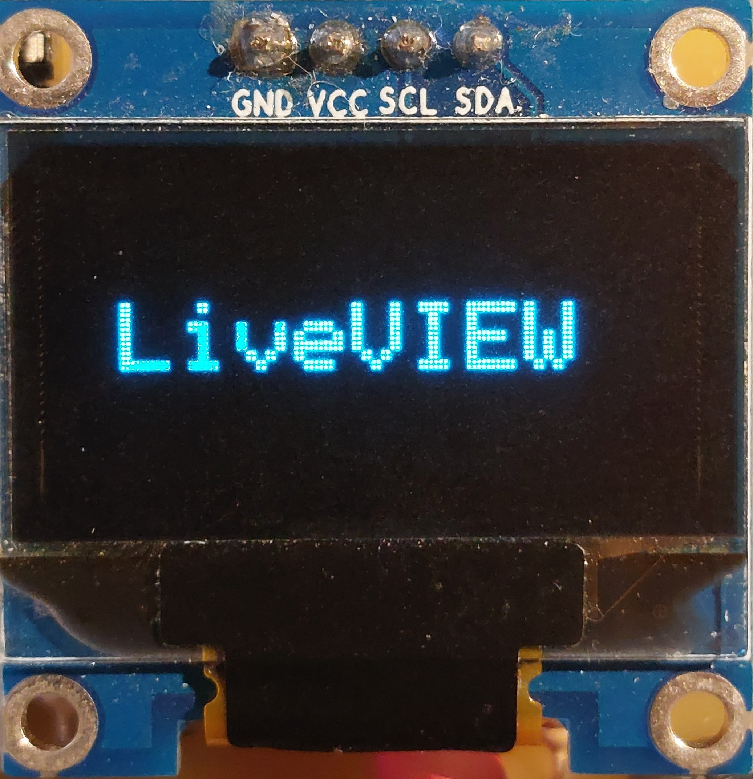
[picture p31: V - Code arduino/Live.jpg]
   
   
 <p><em>Figure 22 : menu de mesure en direct </em></p>
</div>
<div align="justify"> Ce menu permet un affichage en direct de la valeur de résistance lue par l'entrée analogique. Il faut se placer à l'intérieur de ce menu pour utiliser l'application Android car les données sont envoyées au téléphone via le module Bluetooth HC-05. </div>

# VI - L'application Android avec Mit App Inventor

<div align="justify"> Cette application permet de recevoir les données envoyées par le module Bluetooth du PCB et de les afficher sous forme de graphique.

[insérer image explicative]

## A) L'écran de démarrage
<div align="justify"> L'écran de démarrage comporte un seul bouton "Démarrer" sur lequel il suffit de cliquer pour lancer l'application.</div>
<br>
<div align="center">
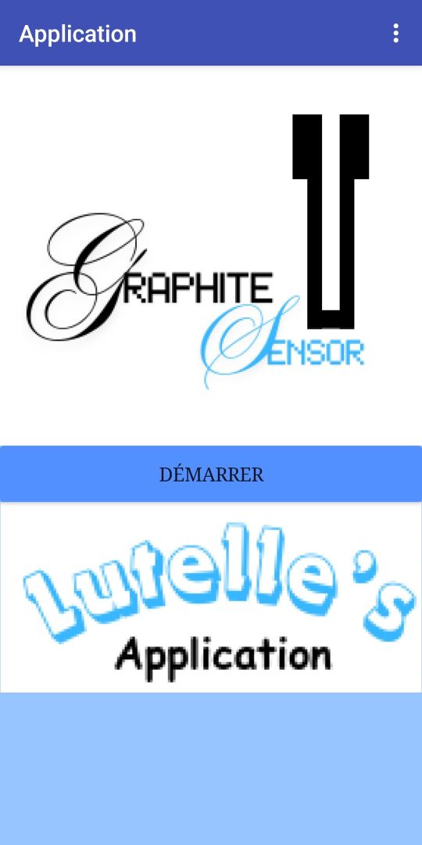
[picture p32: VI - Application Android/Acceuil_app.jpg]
  
  <p><em>Figure 23 : Écran de démarrage de l'application </em></p>
</div>

## B) L'interface principale et ses fonctionnalités

<div align="justify"> Sur le deuxième écran, l'utilisateur doit tout d'abord connecter son téléphone au module Bluetooth pour recevoir les données. Lorsque la connexion est établie, le bouton "Bluetooth connexion" s'affiche en vert. Ensuite, un switch permet de définir quel capteur est utilisé. Si l'on utilise le capteur graphite, il faut renseigner la valeur du potentiomètre numérique dans la case rose pour afficher la bonne valeur de résistance dans la case bleu clair. Par défaut, la valeur de R2 vaut 875 ohms. Un graphique en dessous permet d'afficher en direct les bytes reçus par le module Bluetooth. Les bytes reçus sont également affichés dans la case jaune en dessous du graphique. </div>
<br>
<div align="center">
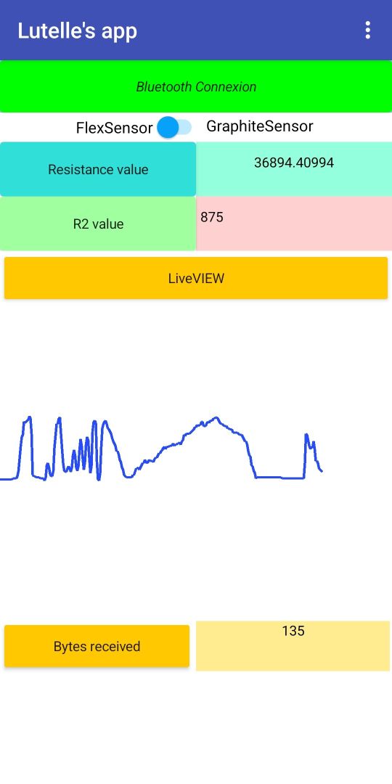
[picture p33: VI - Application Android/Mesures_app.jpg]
  
  <p><em>Figure 24 : Écran pour le relevé de mesures en direct </em></p>
</div>

# VII - Résultats

<div align="justify"> 
Pour réaliser nos mesures, nous avons tracé l'évolution de la variation relative de résistance en fonction de la déformation. Pour la variation relative de résistance, nous appliquons la formule ci-dessous. Rplat correspond à la résistance du capteur graphite sans déformation appliquée et Rcourbé à la résistance mesurée quand le capteur est déformé.
<div align="center">
  
  <p><em>Equation 3 : Formule de la variation relative de résistance</em></p>
</div>
Pour calculer la déformation, nous effectuons le calcul ci-dessous pour tous nos rayons de courbure afin de trouver la déformation correspondante. e correspond à l'épaisseur de la feuille de papier utilisée.
 <div align="center">
  
  <p><em>Equation 4: Formule pour calculer la déformation</em></p>
</div>
Le coefficient de proportionnalité qui lie la variation relative de résistance et la déformation correspond à la <strong>sensibilité</strong> du capteur. 
</div>

<div align="justify">  Pour réaliser tous nos tests nous avons choisi une vitesse de 52% pour le servo moteur. Les crayons testés sont le 6B, 5B, 4B, 3B, B, HB, F et H pour des mesures en tension. Les tests ont été effectués sur chaque rayon de courbure disponible. Pour les mesures en compression, les tests ont été réalisés sur les crayons 6B, 3B et HB pour des rayons de courbure allant jusqu'à 24 mm. Pour <strong> chaque point </strong>, nous avons réalisé 5 mesures de résistance pour un type de crayon et un rayon de courbure donné et pris la moyenne de ces 5 mesures comme résultat final. Au total, pour les mesures en tension cela nous fait 8 (crayons) x 8 (supports) x 5 (mesures pour 1 type de crayon et un rayon de courbure donné) = <strong>320 mesures</strong>. Pour les mesures en compression, nous avons 3 (crayons) x 6 (supports) x 5 (mesures) = <strong>90 mesures</strong>. Nous n'avons pas pu réaliser les mesures en compression pour tous les rayons de courbure disponibles car le capteur se détériorait au fur et à mesure des tests.  Ainsi, pour ce projet nous avons effectué plus de <strong>400</strong> mesures pour caractériser nos capteurs. 
</div>

## A) Les mesures obtenues

<div align="justify"> Voici les résultats de toutes nos mesures en tension (figure 25) et en compression (figure 26). Les courbes obtenues sont cohérentes avec les résultats de Lin, CW., Zhao, Z., Kim, J. et al. En effet, les crayons plus durs comme le 6B possèdent une sensibilité plus faible que les crayons plus légers comme le HB par exemple. Voici le graphique qui regroupe nos résultats pour une déformation en tension.   </div>

<div align="center">
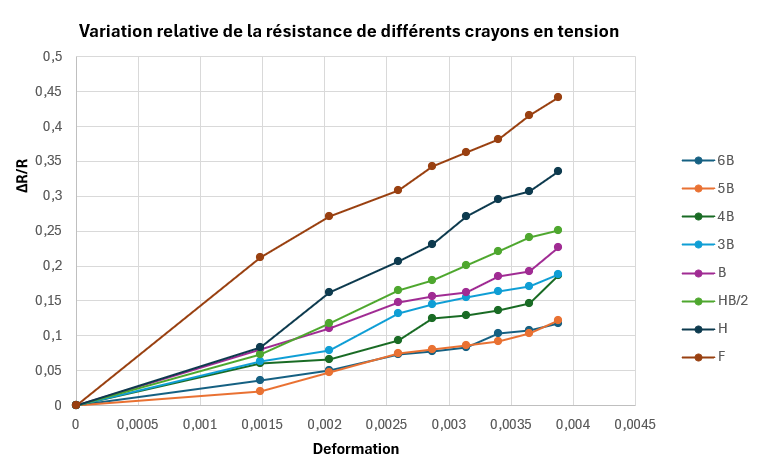
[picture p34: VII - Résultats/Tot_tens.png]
  
  <p><em>Figure 25 : Résultats de la déformation du capteur graphite en tension pour différents crayons</em></p>
</div>

Voici le graphique qui regroupe nos résultats pour une déformation en compression.

<div align="center">
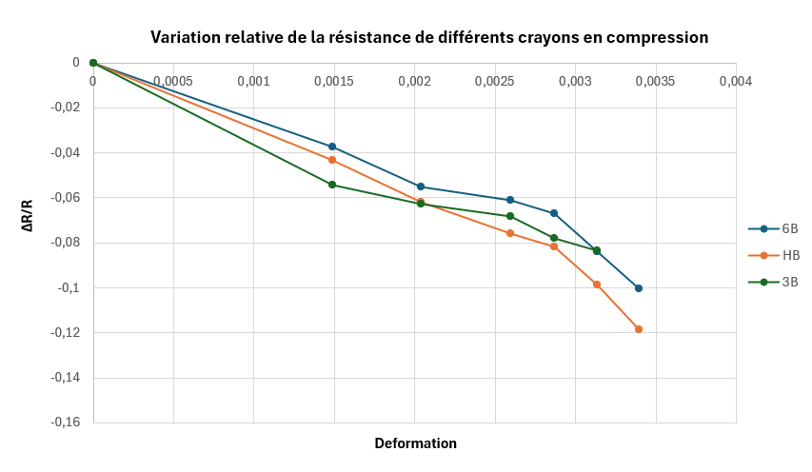
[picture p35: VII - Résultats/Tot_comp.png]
  
  <p><em>Figure 26 : Résultats de la déformation du capteur graphite en compression pour différents crayons</em></p>
</div>

Voici quelques courbes individuelles qui permettent d'apprécier l'évolution linéaire de la variation relative de résistance en fonction de la déformation appliquée.

<div align="center">
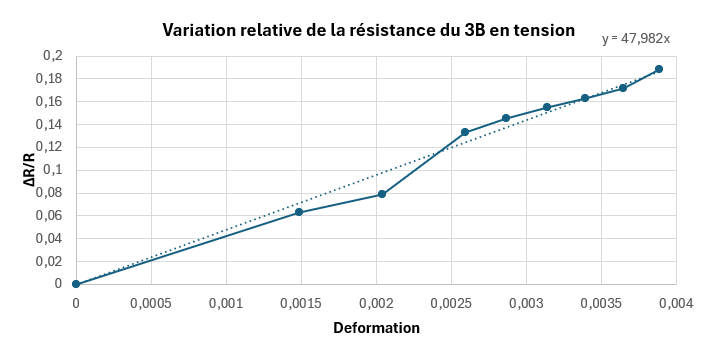
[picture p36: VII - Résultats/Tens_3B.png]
  
  <p><em>Figure 27 : tension du crayon 3B</em></p>
</div>

<div align="center">
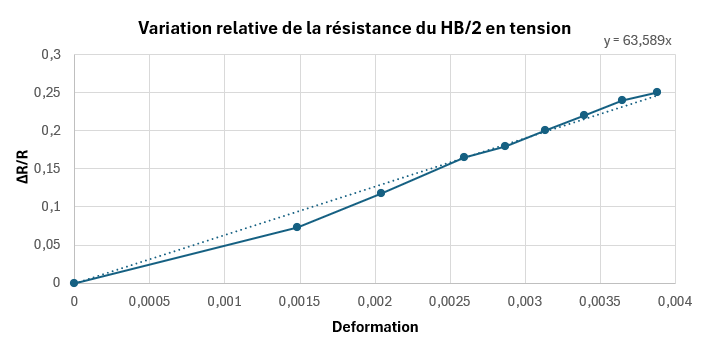
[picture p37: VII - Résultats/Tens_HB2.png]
  
  <p><em>Figure 28 : tension du crayon HB </em></p>
</div>

<div align="center">
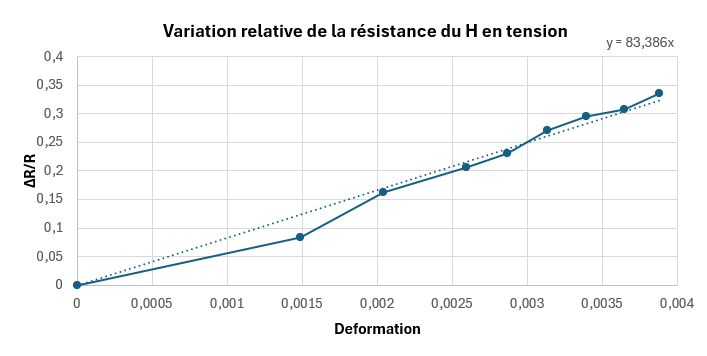
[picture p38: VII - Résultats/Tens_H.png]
  
  <p><em>Figure 29 : tension du crayon H </em></p>
</div>

<div align="center">
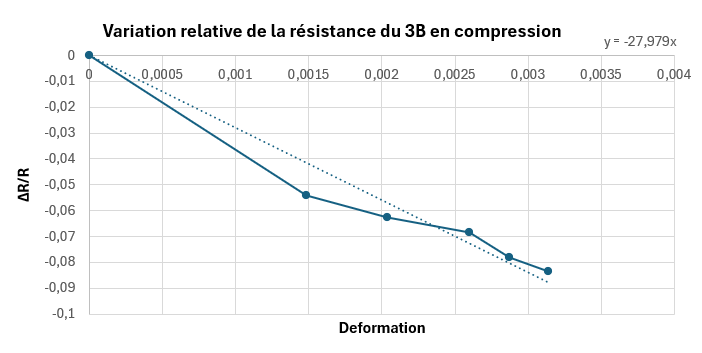
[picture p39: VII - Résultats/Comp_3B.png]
  
  <p><em>Figure 30 : compression du crayon 3B </em></p>
</div>

<div align="center">
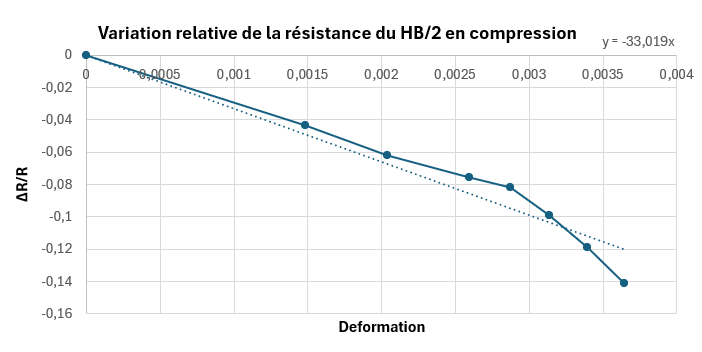
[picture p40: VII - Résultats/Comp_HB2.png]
  
  <p><em>Figure 31 : compression du crayon HB </em></p>
</div>

Nous avons également réalisé nos tests sur le capteur commercial pour pouvoir effectuer une comparaison.

<div align="center">
  
  <p><em>Figure 32 : tension du capteur commercial </em></p>
</div>

Voici un tableau récapitulatif de nos relevés de mesures.

<div align="center">
  
  <p><em>Figure 33 : Sensibilité des capteurs testés </em></p>
</div>

## B) Comparaison avec un capteur commercial: qui sera le meilleur ?
<div align="justify">   Grâce aux résultats ci-dessus, nous pouvons comparer les performances du capteur graphite par rapport au capteur commercial. Ce sont deux capteurs différents qui ont chacun leur propre domaine d'utilisation. Voici les points positifs et négatifs du capteur commercial.
</div>
<br>
 
<div align="center">
<table>
  <thead>
    <tr>
      <th>Points positifs</th>
      <th>Points négatifs</th>
    </tr>
  </thead>
  <tbody>
    <tr>
      <td>Précision importante</td>
      <td>Impossible de faire une mesure en compression</td>
    </tr>
    <tr>
      <td>Sensibilité élevée</td>
      <td>Coûte beaucoup plus cher qu'un capteur graphite (10 euros environ)</td>
    </tr>
   <tr>
      <td>Réutilisable un grand nombre de fois sans détérioration</td>
      <td></td>
    </tr>
  </tbody>
</table>
</div>
 
 De même, voici un tableau qui récapitule les avantages et inconvénients du capteur graphite.
 
 <div align="center">
<table>
  <thead>
    <tr>
      <th>Points positifs</th>
      <th>Points négatifs</th>
    </tr>
  </thead>
  <tbody>
    <tr>
      <td>Sensibilité qui peut rivaliser avec celle du capteur commercial selon le type de crayon utilisé</td>
      <td>Manipulation délicate car le capteur se détériore au moindre contact</td>
    </tr>
    <tr>
      <td>Permet de réaliser des mesures en compression</td>
      <td>Si le capteur est courbé trop de fois les fibres du papiers se cassent ce qui nuit à la mesure</td>
    </tr>
  </tbody>
</table>
</div>

<div align="justify"> Pour conclure, le capteur graphite a une gamme d'utilisation plus large que le capteur commercial. Sa sensibilité peut égaler celle du capteur commercial. Il reste cependant très délicat et contraignant à manipuler. Nous pensons qu'une piste d'amélioration possible pour ce capteur serait d'envisager un moyen de l'encapsuler pour protéger le graphite. Avec une telle solution, il serait possible de l'industrialiser pour le rendre plus durable. Toutefois, la solution ne devra pas être trop coûteuse pour ne pas perdre l'intérêt de ce capteur qui se veut low-tech avant tout.
</div>

# Contacts

Estelle AUBRY:<a> eaubry@insa-toulouse.fr</a>

Lucas BOURDARIE:<a> bourdari@insa-toulouse.fr</a>

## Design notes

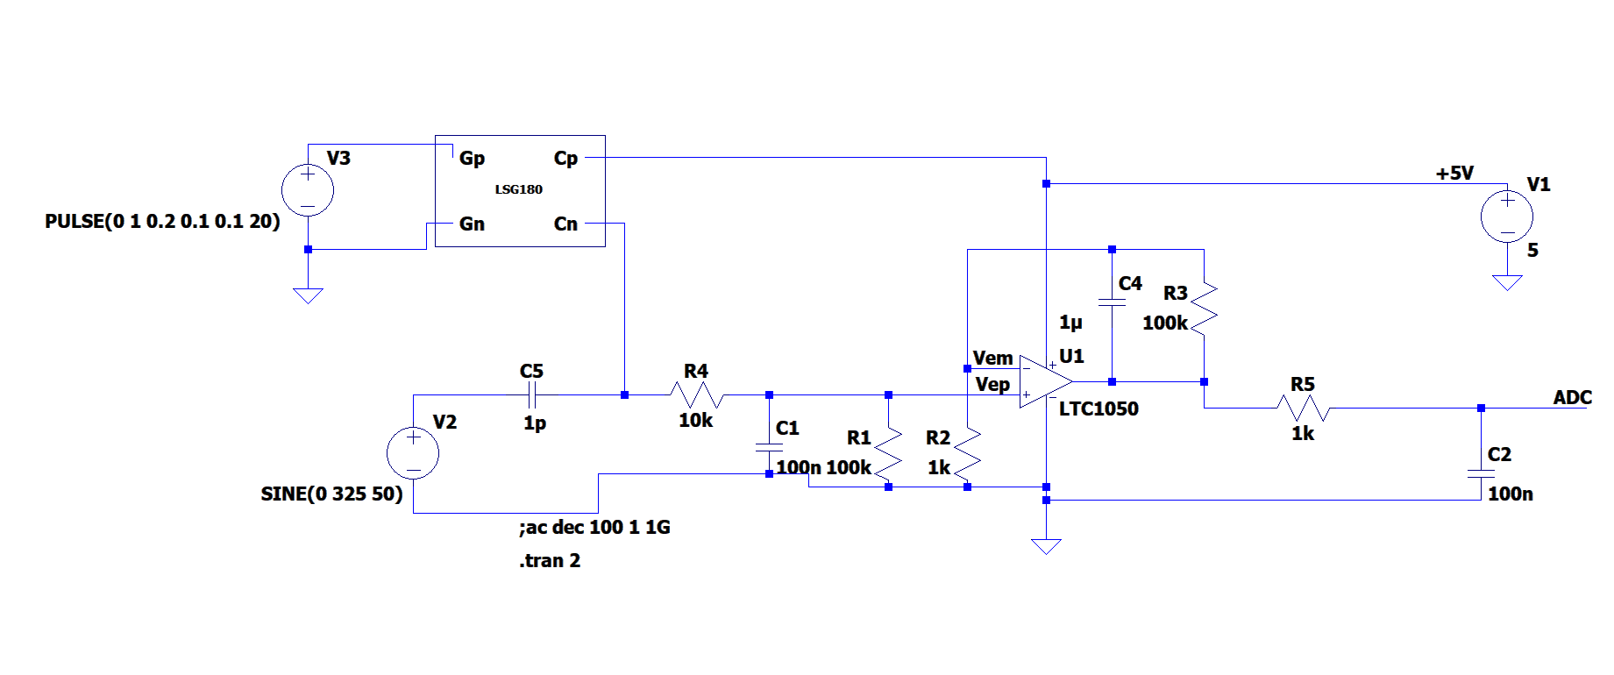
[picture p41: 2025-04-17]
II - Simulation/Capture_ltspice_Sans_condo_5V_sans_fond.PNG

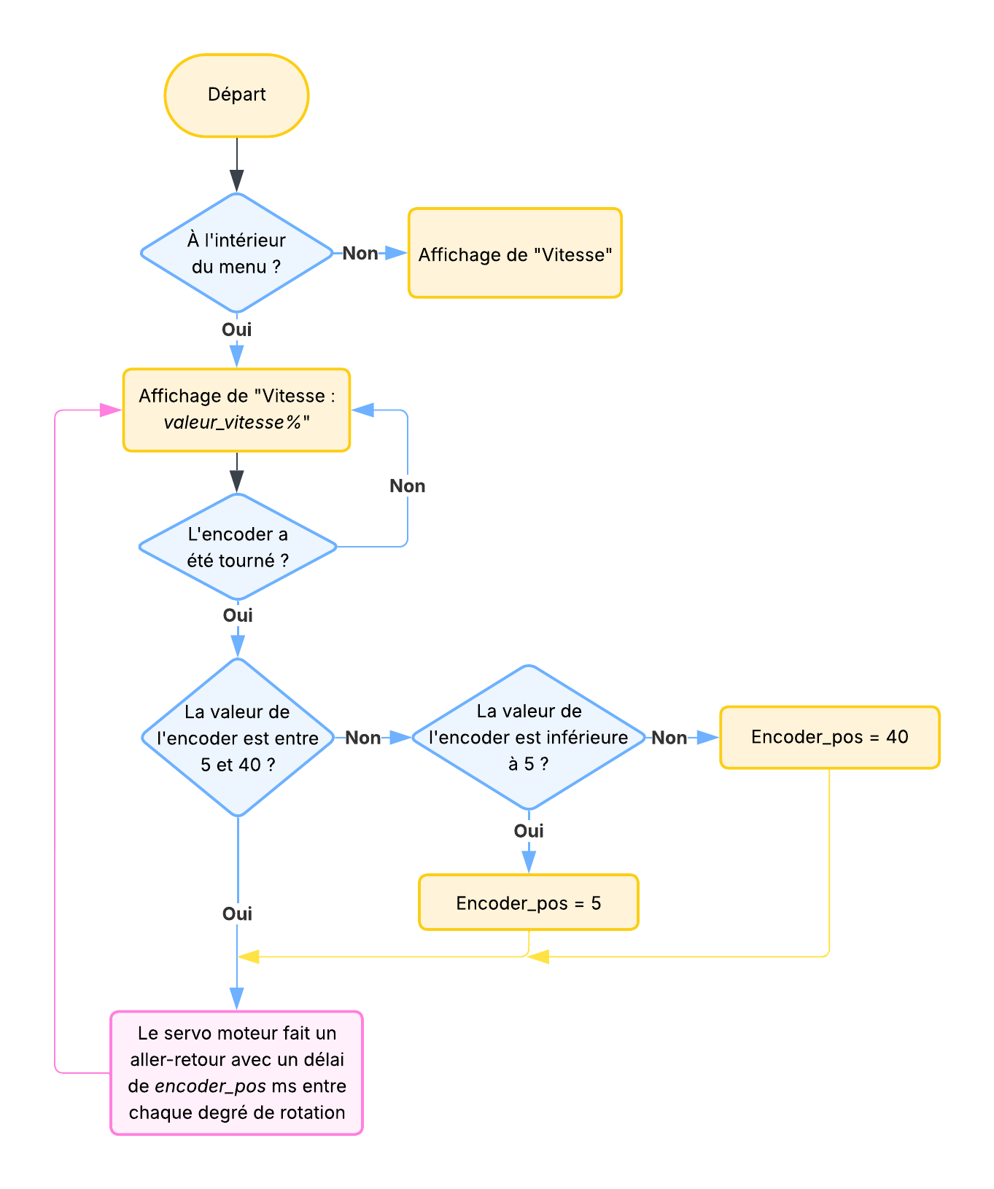
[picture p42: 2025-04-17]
V - Code arduino/Vitesse.png

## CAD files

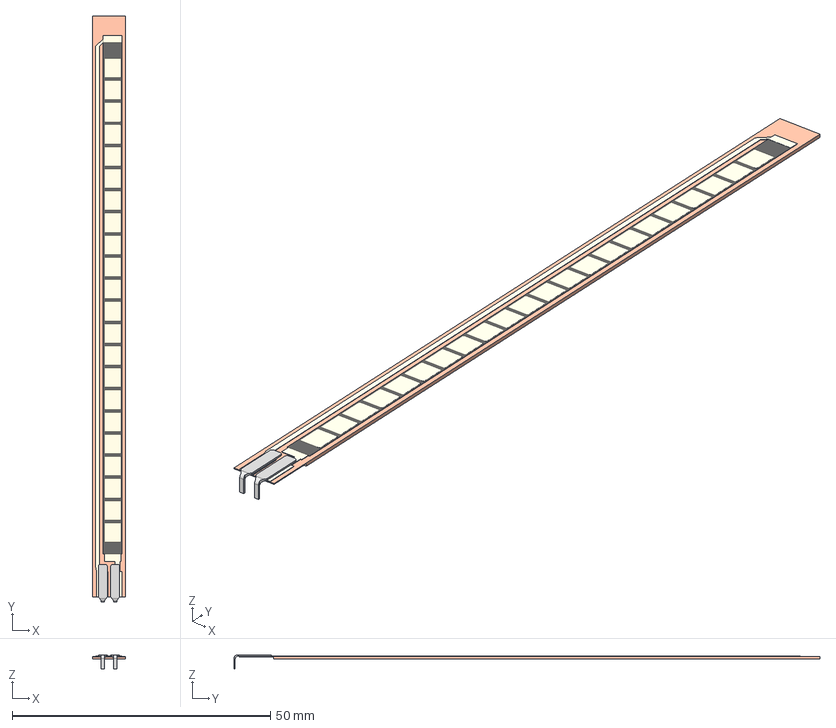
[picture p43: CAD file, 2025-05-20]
III - KiCAD/PCB_design/FS-L-0095-103-ST - Assembly.stp
6.45 x 113.5 x 2.77 mm
FS-L-0095-103-ST - Base
FS-L-0095-103-ST - Top

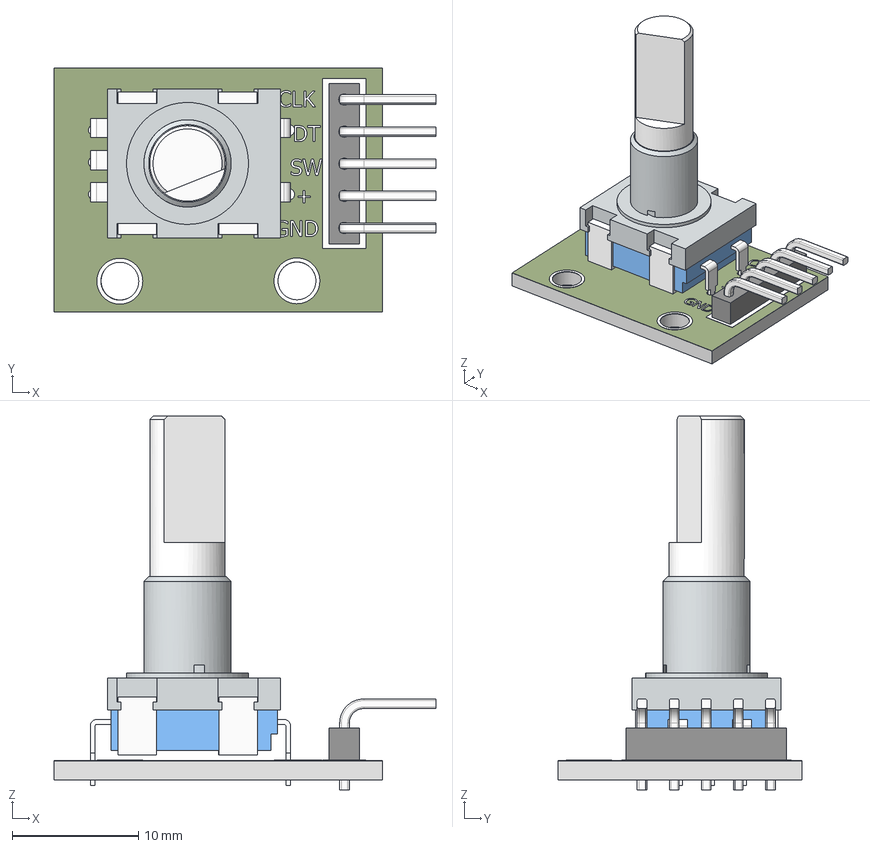
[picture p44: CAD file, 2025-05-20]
III - KiCAD/PCB_design/rotary+encoder_14mm_hole_spc.stp
30.2 x 19.3 x 29.6 mm
pcb
mtg flange
body_encoder
5 pin header
90d pin_header x 5
decal_encoder
pins_encoder body_2 x 5
shaft_encoder

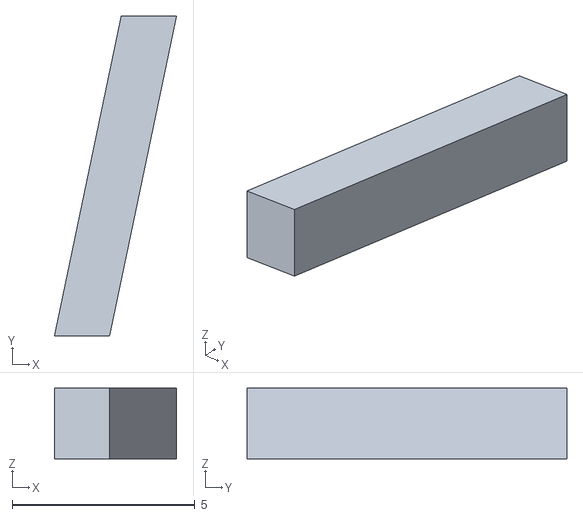
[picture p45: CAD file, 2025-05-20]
IV - Banc de test/Modelisation_3D/l.stl
3.35 x 8.76 x 1.93

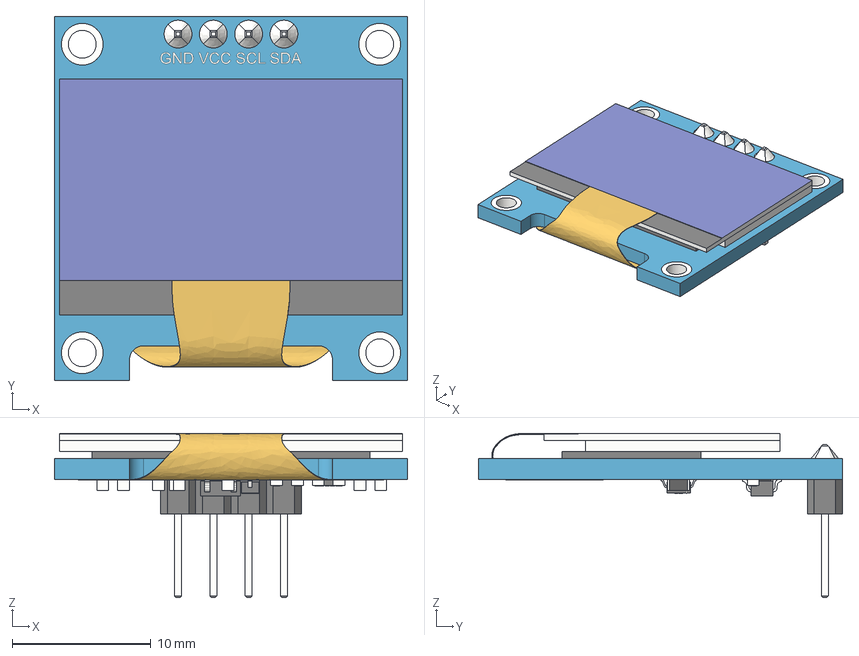
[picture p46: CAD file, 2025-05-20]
III - KiCAD/PCB_design/SSD1306_OLED_Display(128x64).step
25.4 x 26.2 x 11.8 mm
board
screen
pin_header
soldering
smd_capacitor
smd_capacitor (1)
914_smd_resistor
472_smd_resistor x 3
t4_smd_diode
smd_capacitor (2)
smd_capacitor (3)
smd_capacitor (4)
smd_capacitor (5)
smd_capacitor (6)
472_smd_resistor (1)
SOT-23_XC6206 v3
smd_capacitor (7)
flat_cable

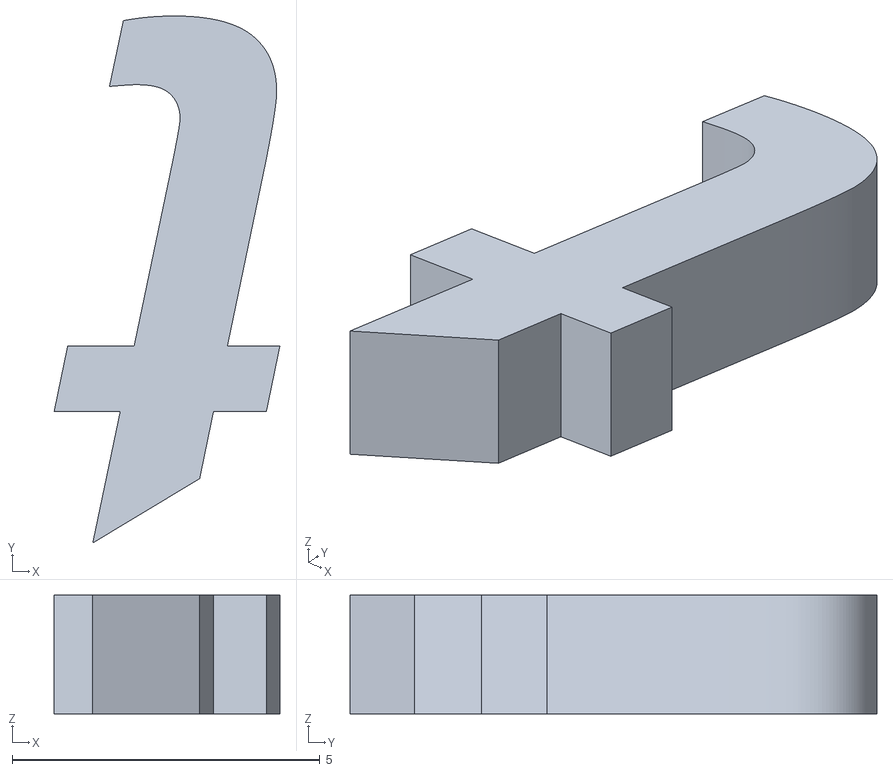
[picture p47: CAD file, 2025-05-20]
IV - Banc de test/Modelisation_3D/t.stl
3.67 x 8.57 x 1.93

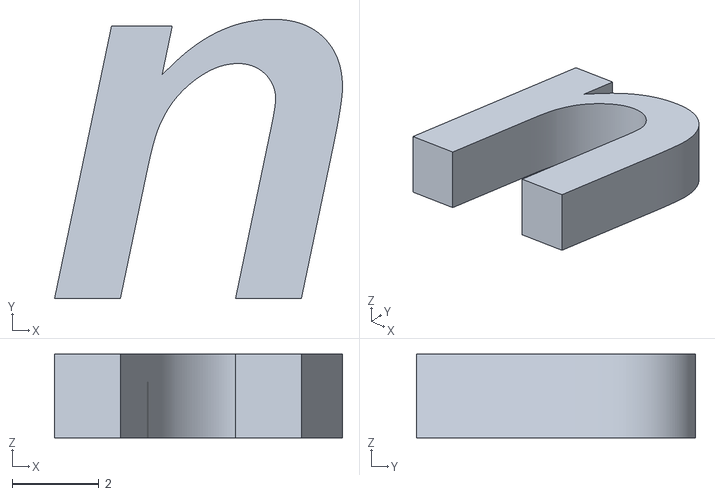
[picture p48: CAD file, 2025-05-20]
IV - Banc de test/Modelisation_3D/u.stl
6.63 x 6.43 x 1.93

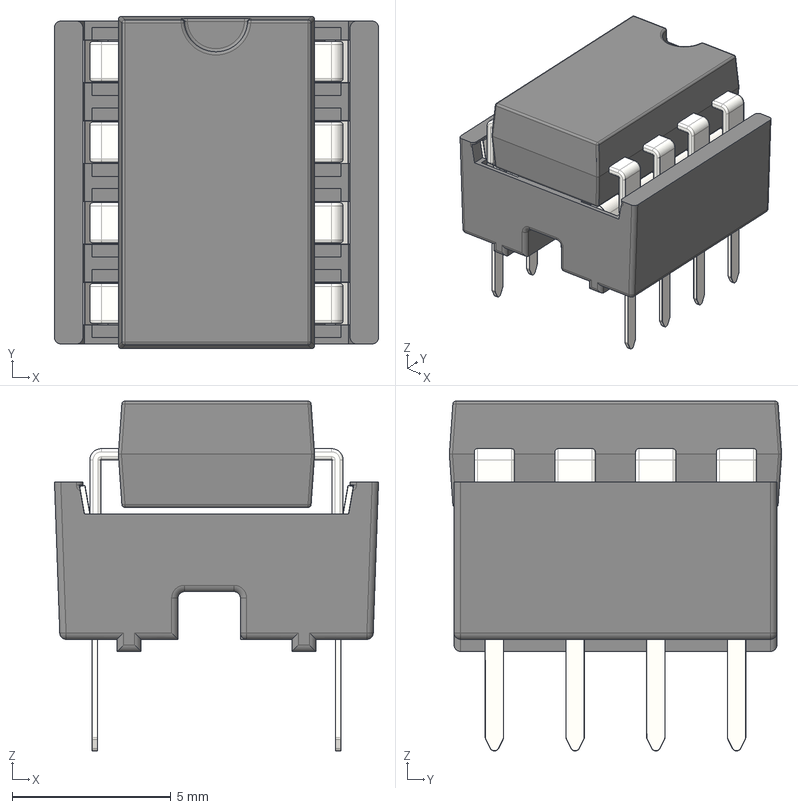
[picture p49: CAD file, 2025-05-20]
III - KiCAD/PCB_design/DIP-8 W7.62mm IC with Socket.stp
10.2 x 10.5 x 11.0 mm
Stamped Dual Wipe Contact for DIP Sockets x 8
Body DIP-8 P7.62mm Socket
IC Beinchen x 8
DIP-8 W7.62

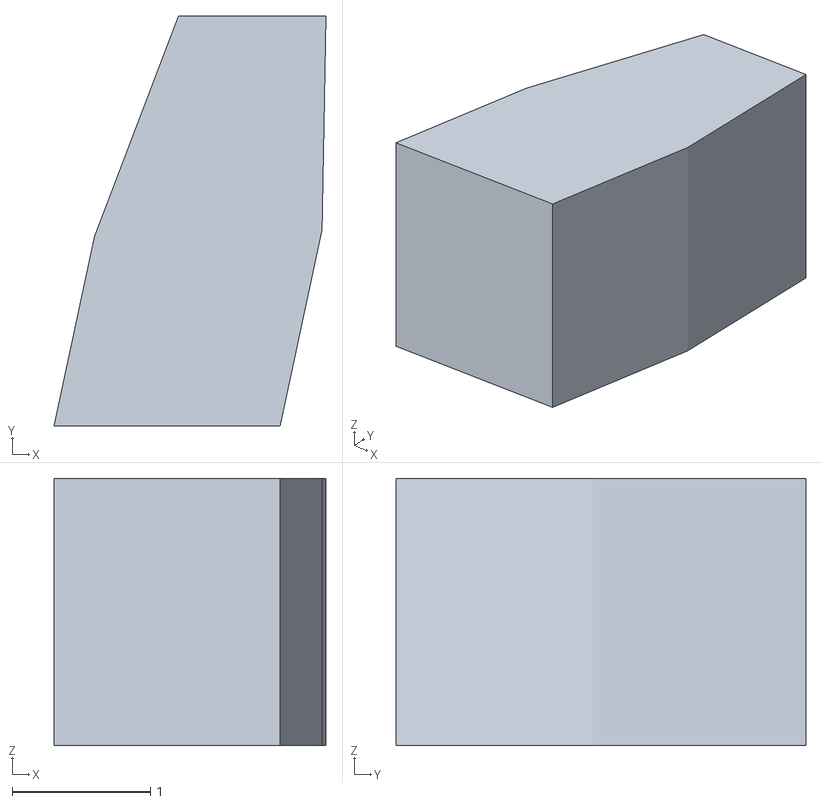
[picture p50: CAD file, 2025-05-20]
IV - Banc de test/Modelisation_3D/'.stl
1.96 x 2.96 x 1.93

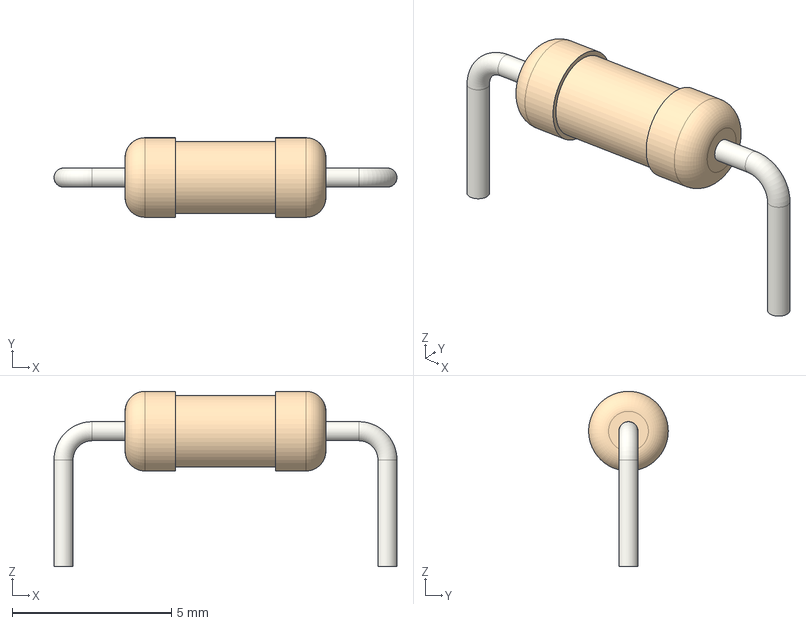
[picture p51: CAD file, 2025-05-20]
III - KiCAD/PCB_design/R_Axial_DIN0207_L6.3mm_D2.5mm_P10.16mm_Horizontal.step
10.8 x 2.50 x 5.50 mm

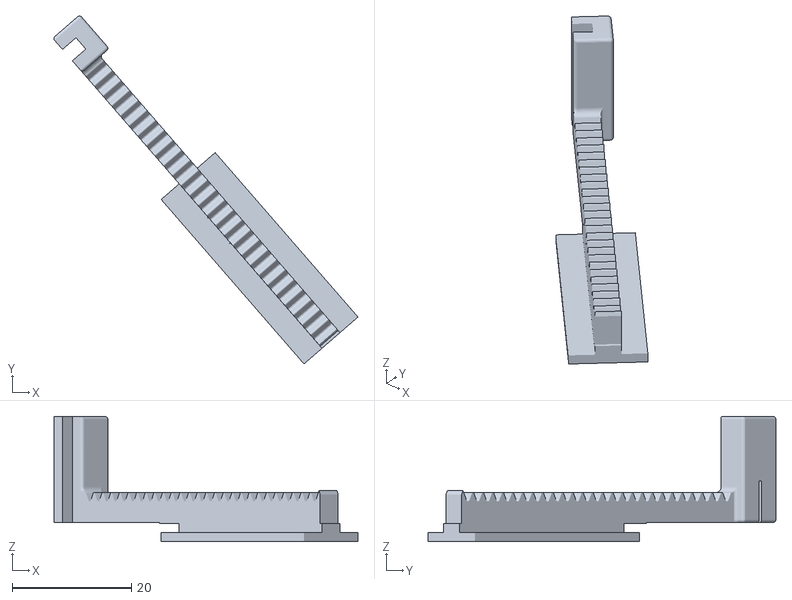
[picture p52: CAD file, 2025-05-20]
IV - Banc de test/Modelisation_3D/glissiere.stl
51.0 x 58.4 x 21.0

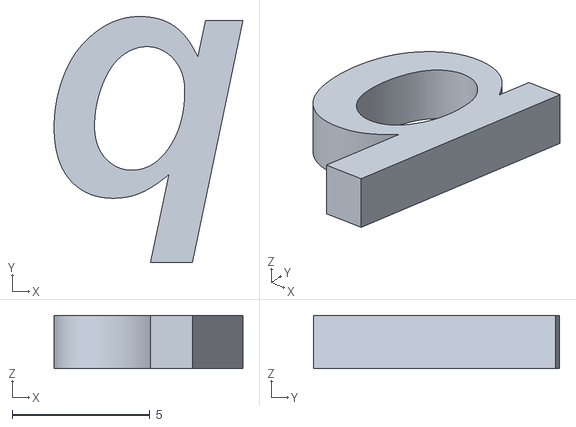
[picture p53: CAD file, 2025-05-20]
IV - Banc de test/Modelisation_3D/b.stl
6.84 x 8.91 x 1.93

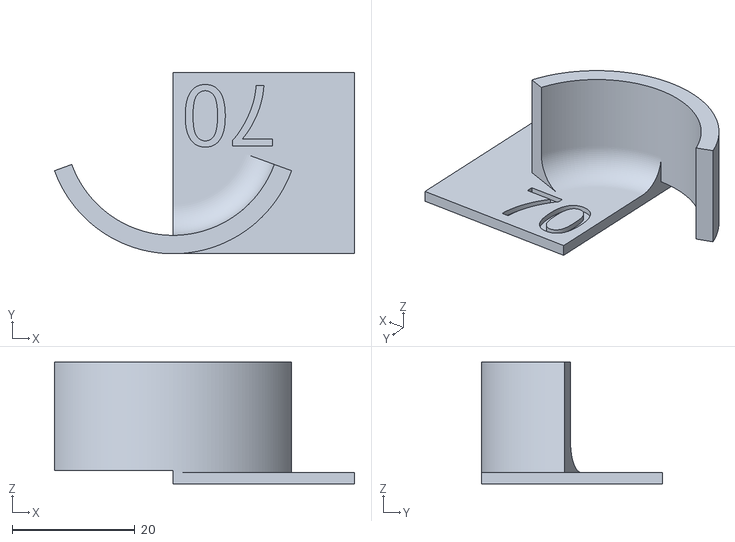
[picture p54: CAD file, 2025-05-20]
IV - Banc de test/Modelisation_3D/70.stl
48.9 x 29.6 x 19.9

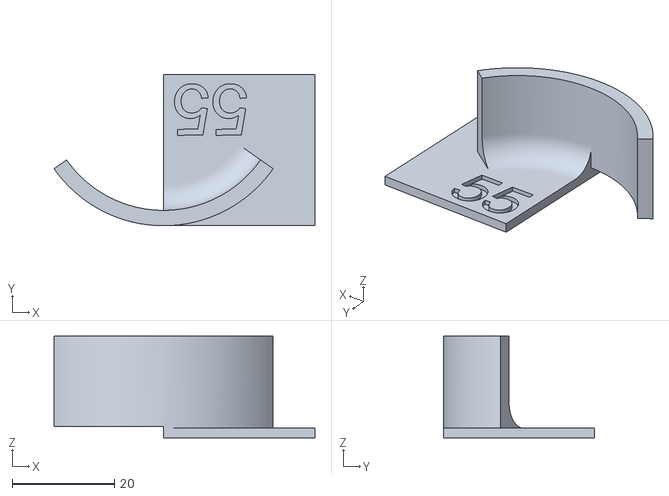
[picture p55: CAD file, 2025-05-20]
IV - Banc de test/Modelisation_3D/55.stl
51.0 x 29.6 x 19.9

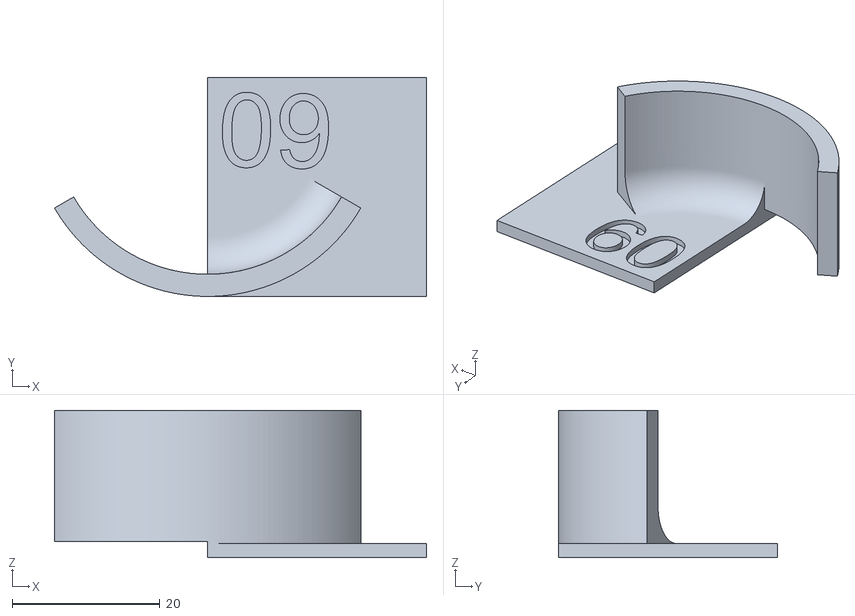
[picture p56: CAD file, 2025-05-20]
IV - Banc de test/Modelisation_3D/60.stl
50.3 x 29.6 x 19.9

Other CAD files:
IV - Banc de test/Modelisation_3D/Grand_L.stl
IV - Banc de test/Modelisation_3D/Support.stl
IV - Banc de test/Modelisation_3D/65.stl
IV - Banc de test/Modelisation_3D/c.stl
IV - Banc de test/Modelisation_3D/30.stl
IV - Banc de test/Modelisation_3D/40.stl
IV - Banc de test/Modelisation_3D/50.stl
IV - Banc de test/Modelisation_3D/75.stl
IV - Banc de test/Modelisation_3D/Grand_T.stl
IV - Banc de test/Modelisation_3D/e.stl

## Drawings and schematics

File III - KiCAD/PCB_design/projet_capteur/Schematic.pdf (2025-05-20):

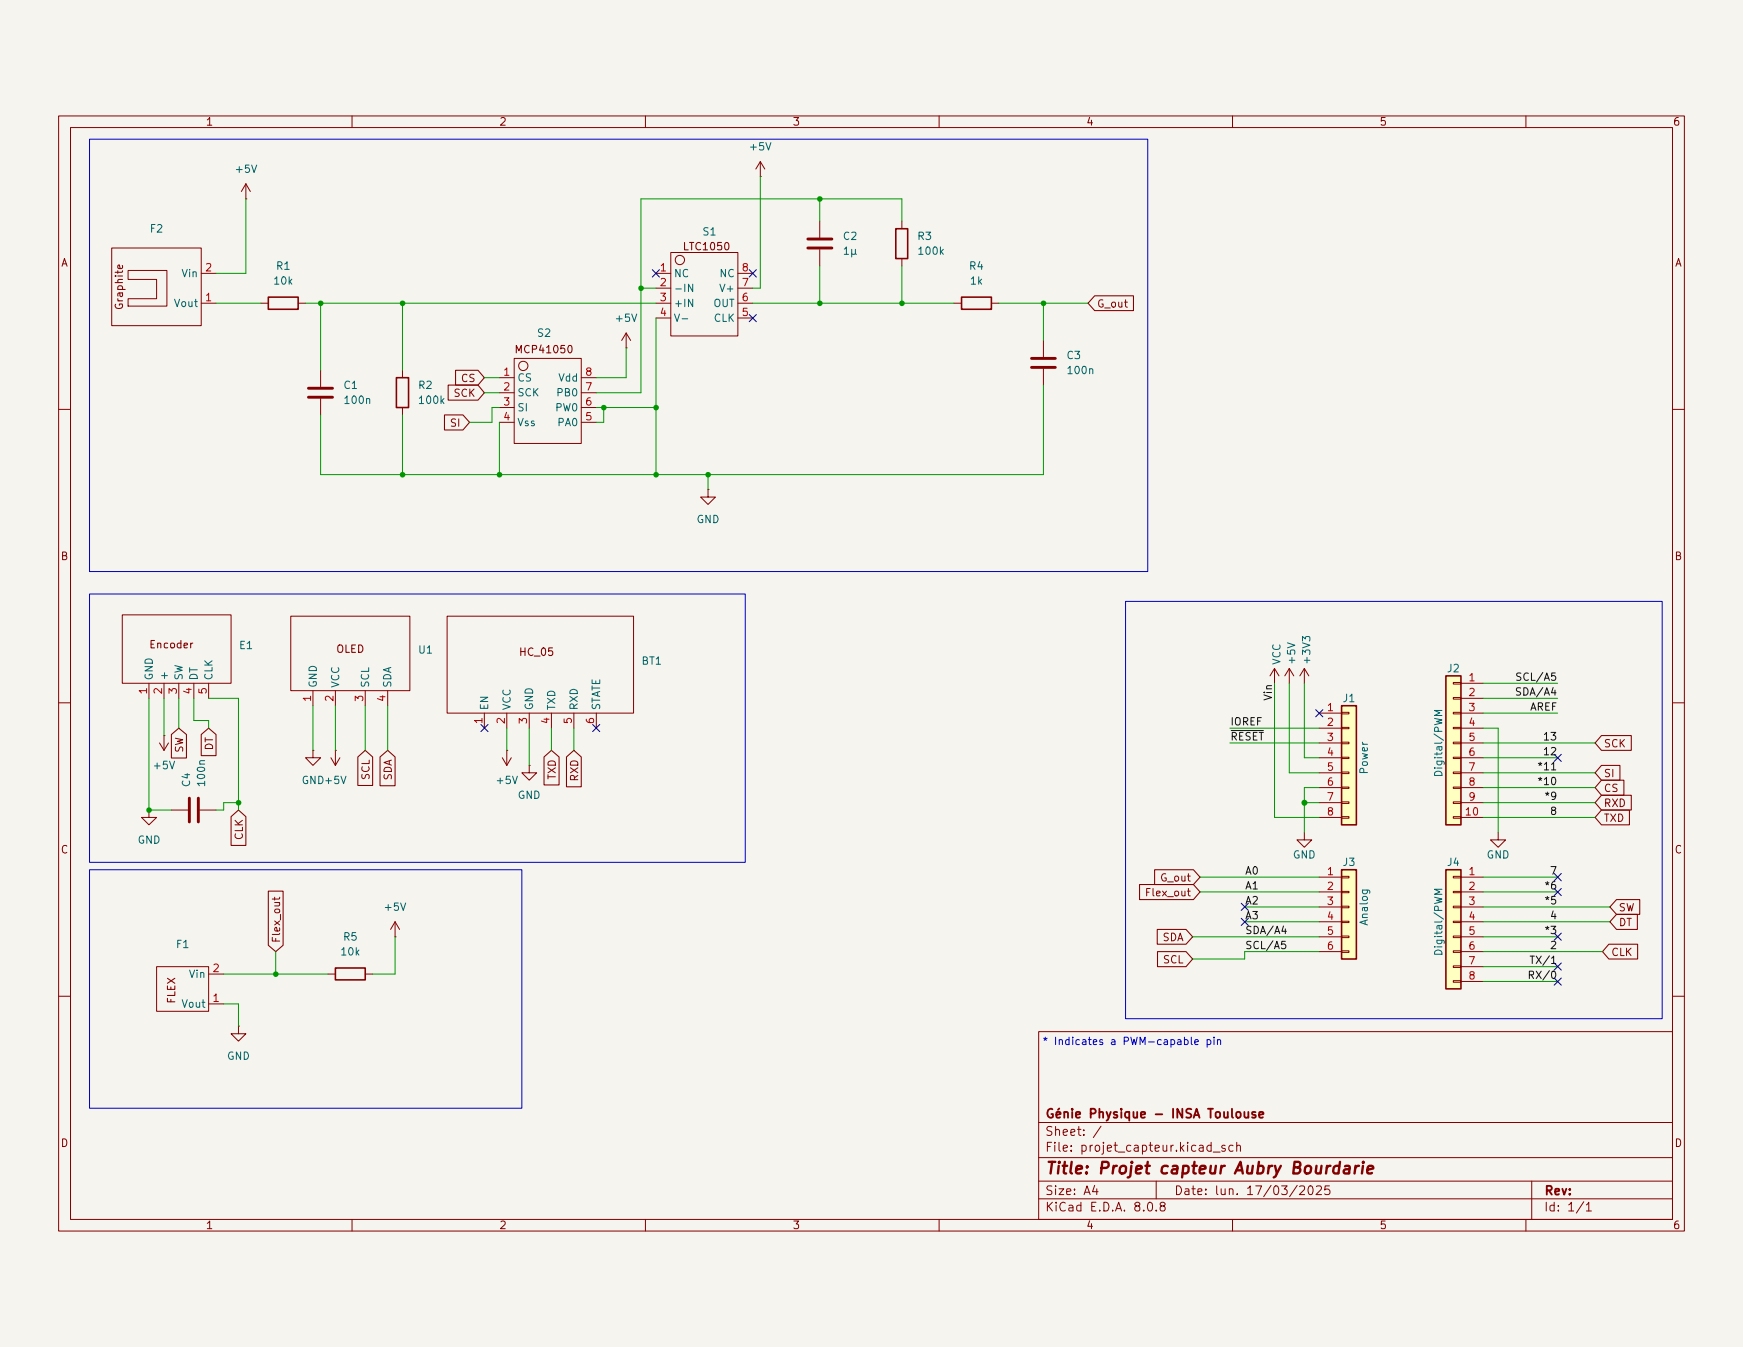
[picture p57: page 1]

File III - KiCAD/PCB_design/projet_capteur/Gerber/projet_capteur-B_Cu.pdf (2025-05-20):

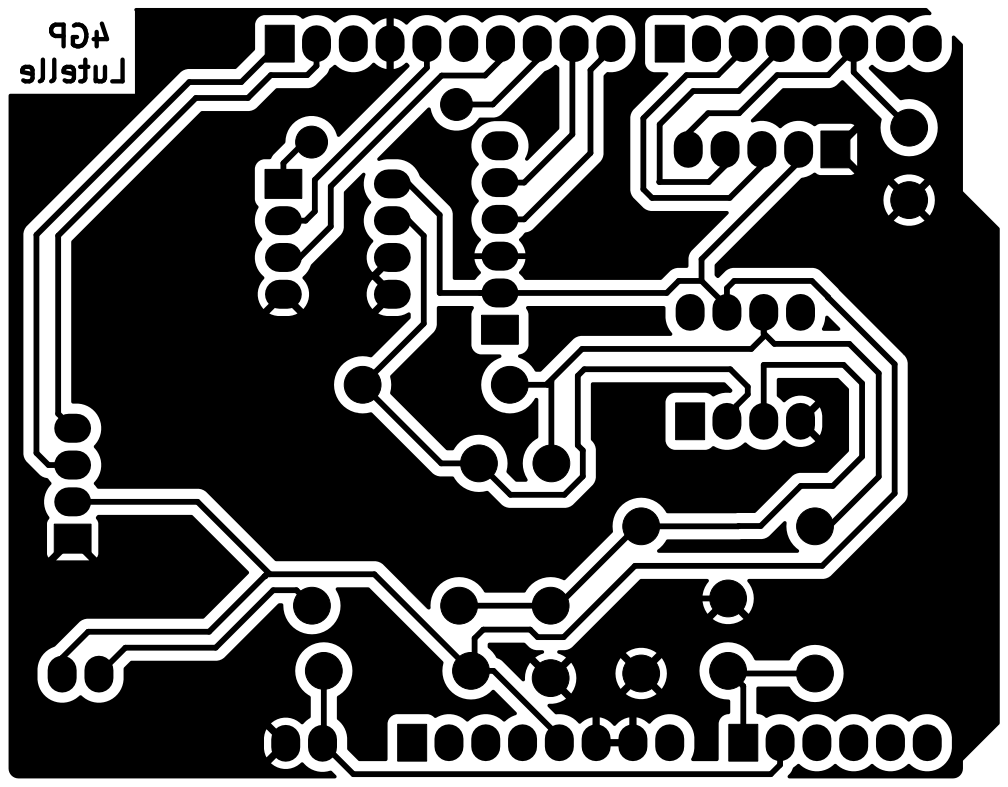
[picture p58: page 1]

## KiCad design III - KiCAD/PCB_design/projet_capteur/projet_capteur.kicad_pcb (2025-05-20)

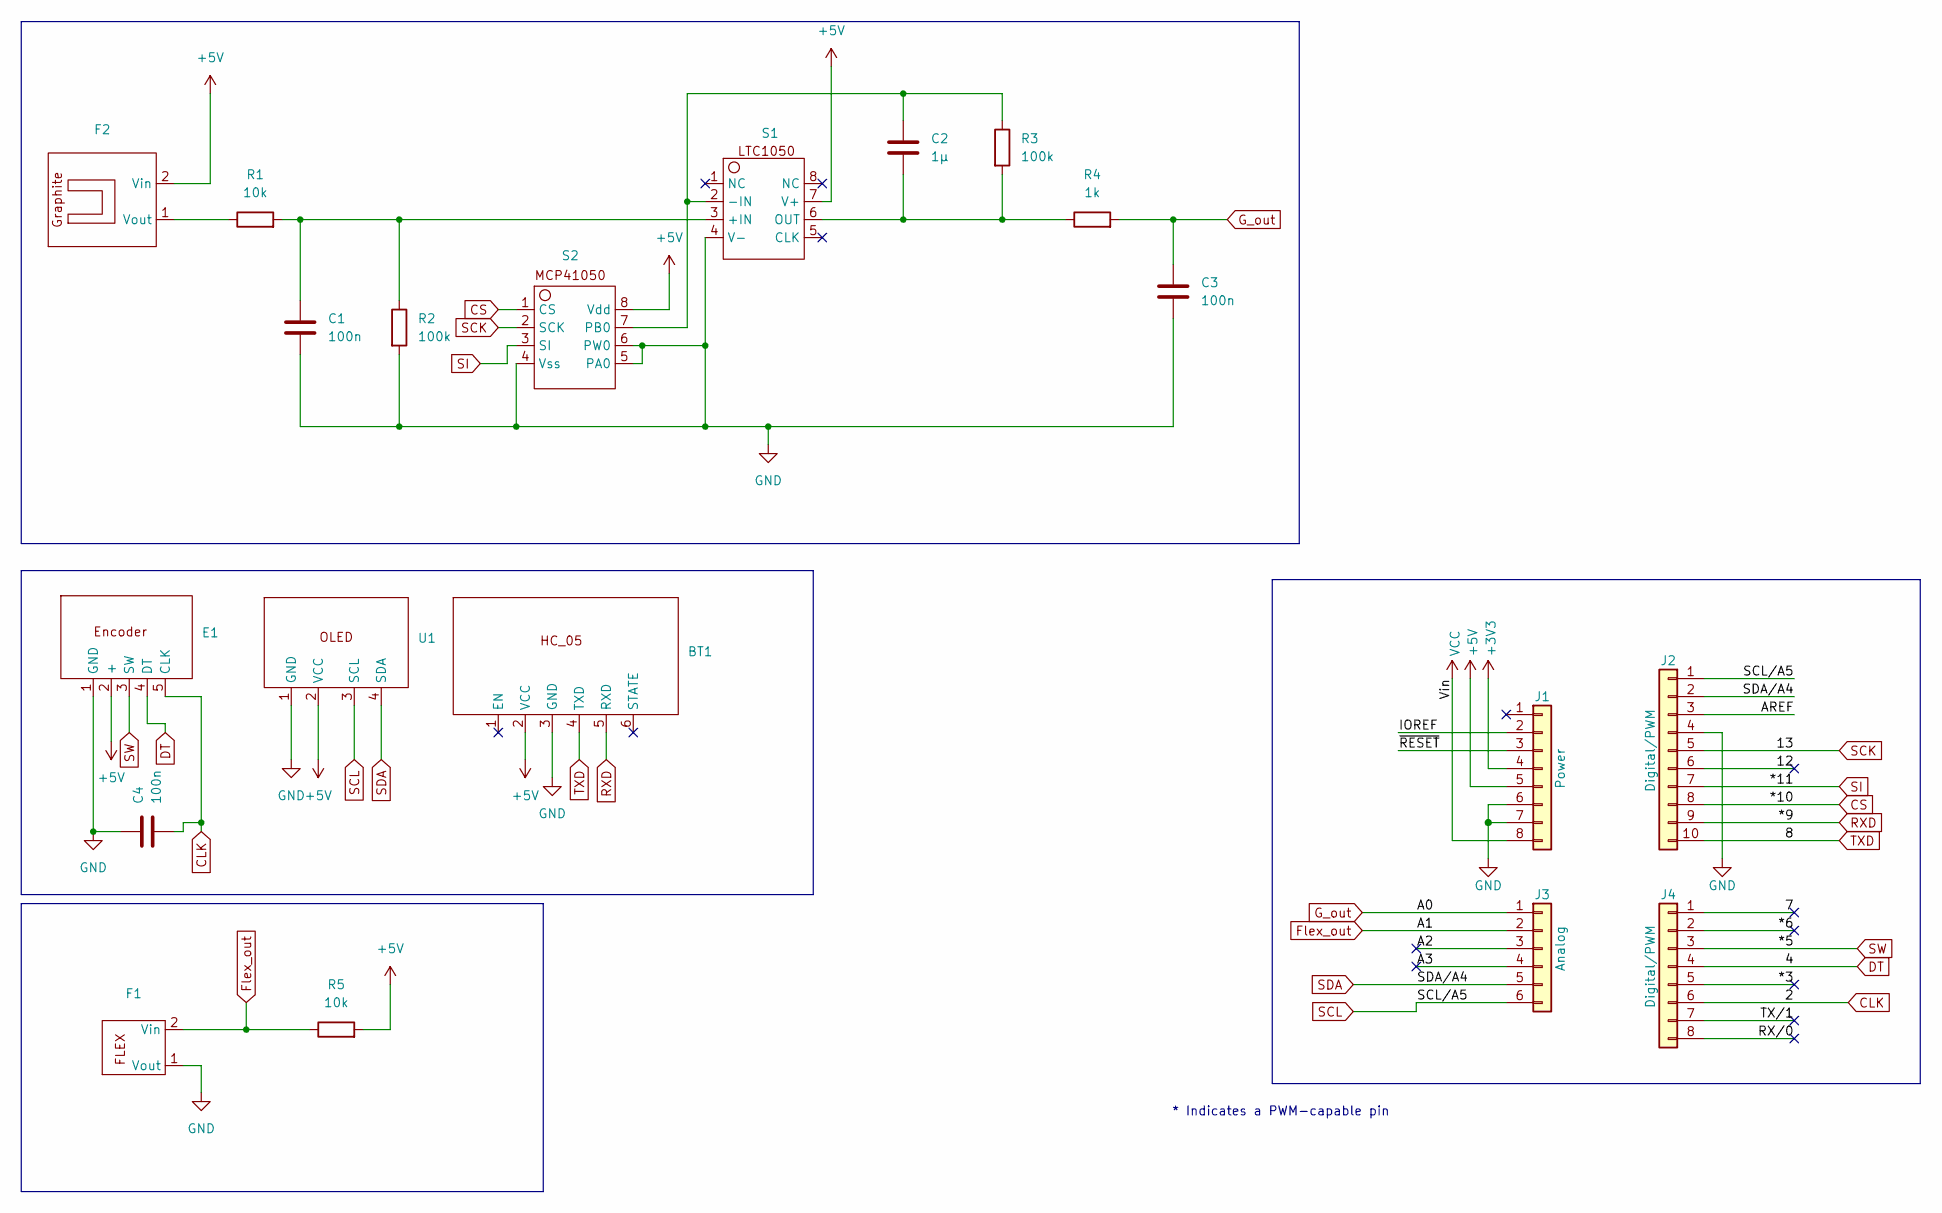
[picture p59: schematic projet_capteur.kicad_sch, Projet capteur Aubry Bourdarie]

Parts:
BT1: SIP-6
C1, C3, C4: 100n; C_Disc_D4.3mm_W1.9mm_P5.00mm
C2: 1µ; C_Rect_L7.0mm_W4.5mm_P5.00mm
E1: Encoder
F1, F2: Flex_sens
J1: Power; PinSocket_1x08_P2.54mm_Vertical
J2: Digital/PWM; PinSocket_1x10_P2.54mm_Vertical
J3: Analog; PinSocket_1x06_P2.54mm_Vertical
J4: Digital/PWM; PinSocket_1x08_P2.54mm_Vertical
R1, R5: 10k; Resistance
R2, R3: 100k; Resistance
R4: 1k; Resistance
S1, S2: Support_ampli
U1: SIP-4

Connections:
+3V3: J1.4
+5V: BT1.2 (VCC), E1.2 (+), F2.2 (Vin), J1.5, R5.2, S1.7 (V+), S2.8 (Vdd), U1.2 (VCC)
/7: J4.1
/12: J2.6
/*3: J4.5
/*6: J4.2
/A2: J3.3
/A3: J3.4
/AREF: J2.3
/IOREF: J1.2
/RX/0: J4.8
/TX/1: J4.7
/~RESET: J1.3
CLK: C4.2, E1.5 (CLK), J4.6
CS: J2.8, S2.1 (CS)
DT: E1.4 (DT), J4.4
Flex_out: F1.2 (Vin), J3.2, R5.1
GND: BT1.3 (GND), C1.2, C3.2, C4.1, E1.1 (GND), F1.1 (Vout), J1.6, J1.7, J2.4, R2.2, S1.4 (V-), S2.4 (Vss), S2.5 (PA0), S2.6 (PW0), U1.1 (GND)
G_out: C3.1, J3.1, R4.2
unnamed: F2.1 (Vout), R1.1
unnamed: C1.1, R1.2, R2.1, S1.3 (+IN)
unnamed: C2.1, R3.1, S1.2 (-IN), S2.7 (PB0)
unnamed: C2.2, R3.2, R4.1, S1.6 (OUT)
RXD: BT1.5 (RXD), J2.9
SCK: J2.5, S2.2 (SCK)
SCL: J2.1, J3.6, U1.3 (SCL)
SDA: J2.2, J3.5, U1.4 (SDA)
SI: J2.7, S2.3 (SI)
SW: E1.3 (SW), J4.3
TXD: BT1.4 (TXD), J2.10
VCC: J1.8

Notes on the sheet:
* Indicates a PWM-capable pin

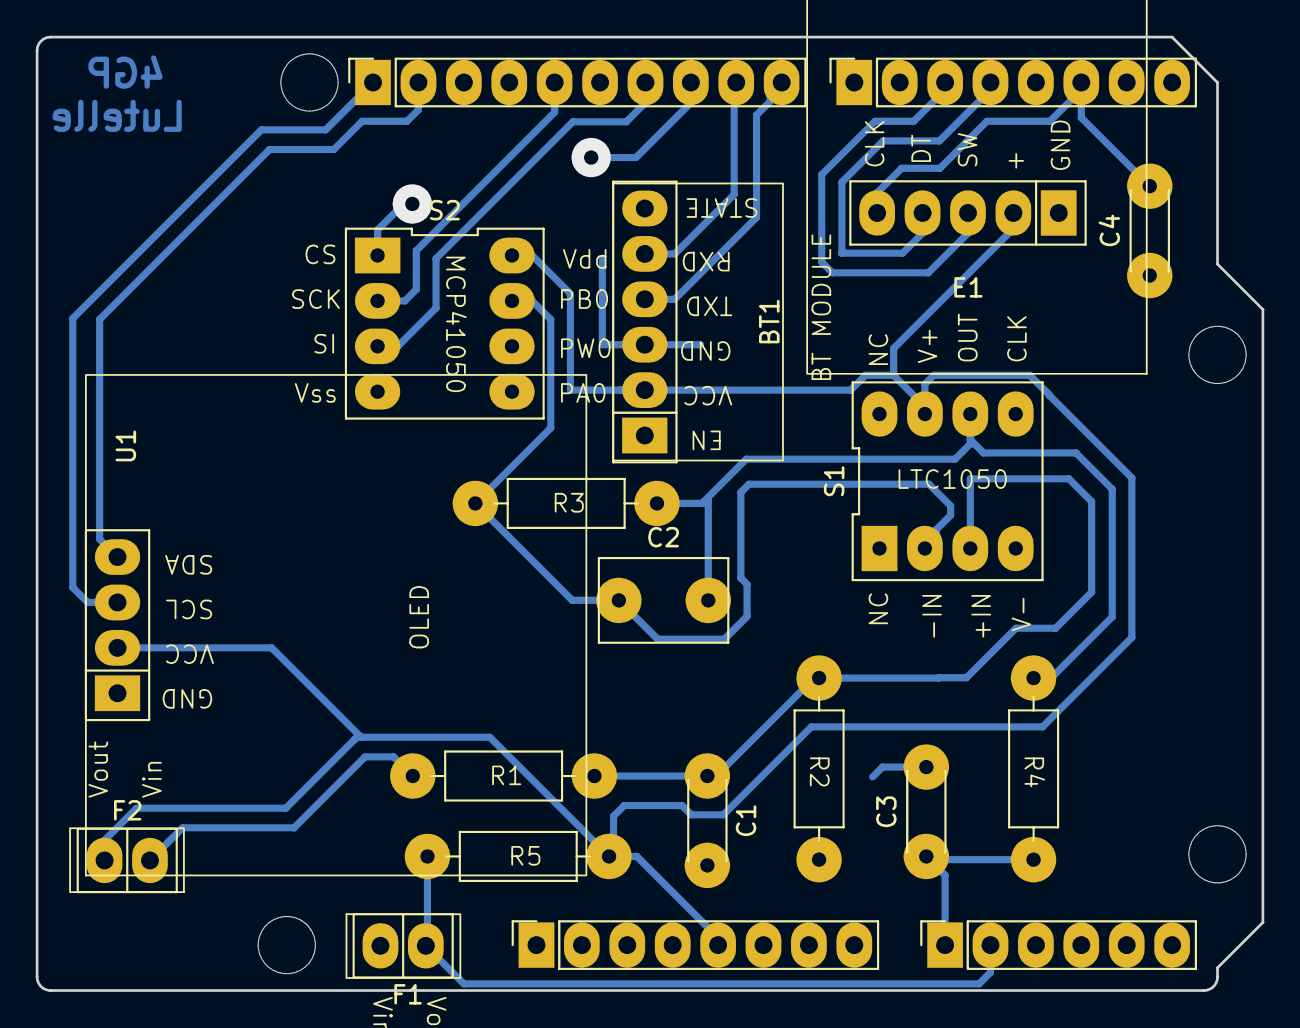
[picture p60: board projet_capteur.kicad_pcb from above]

Board: 2 copper layers, 68.6 x 53.3 mm, 24 parts (0 on the bottom side), 18 nets.

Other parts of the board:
MH1, MH2, MH3, MH4: MountingHole_3.2mm

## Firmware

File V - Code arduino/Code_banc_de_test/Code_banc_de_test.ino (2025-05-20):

#include <Adafruit_SSD1306.h>            //Librairie pour l'écran OLED
#include <Fonts/FreeSerifItalic9pt7b.h>  //Librairie pour changer la police de l'écran OLED
#include <SoftwareSerial.h>              //Librairie pour la communication bluetooth
#include <SPI.h>                         //Librairie pour gérer la communication en SPI avec le potentiomètre digital
#include <Servo.h>                       //Librairie pour gérer la rotation du servo moteur

//Bluetooth
#define rxPin 8
#define txPin 9

//Flex sensor
#define flexPin A1

//Graphite sensor
#define graphite A0

//Encoder
#define encoder0PinA 2
#define encoder0PinB 4
#define Switch 5

//OLED
#define nombreDePixelsEnLargeur 128
#define nombreDePixelsEnHauteur 64
#define brocheResetOLED -1
#define adresseI2CecranOLED 0x3C
Adafruit_SSD1306 ecranOLED(nombreDePixelsEnLargeur, nombreDePixelsEnHauteur, &Wire, brocheResetOLED);

//Encoder
volatile int encoder_pos = 0;
int buttonState;
int lastButtonState = LOW;
long lastDebounceTime = 0;
long debounceDelay = 80;
int previous_reading = 1;
bool in_menu = false;
bool utiliser_graphite = 1;
int nmbre_repet = 1;


//Servo
int pos_servo = 90;
Servo myservo;
int valeur_borne = 180;
int val_vit = 40;

//Bluetooth
SoftwareSerial mySerial(rxPin, txPin);

//Flex
const float VCC = 5.0;
const float R = 33000.0;
const float flatR = 30900;
const float bendR = 63000;
int Valeur_flex;
float V_value_flex;
byte Valeur_flex_send;
float V_value;
float R_value;
float angle;

//Potentiometer digital
const byte csPin = 10;
const int maxPositions = 256;
const long rAB = 48000;
const byte rWiper = 125;
const byte pot0 = 0x11;
const byte pot0Shutdown = 0x21;
float res_pot = 0;
int R2_pos = 0;

//Graphite sensor
int Valeur_graphite;
byte Valeur_graphite_send;
float V_value_graph;
float resistance;
const float R1 = 100000.0;
const float R3 = 100000.0;
const float R5 = 10000.0;

//Permet de mettre à jour la valeur de la position de l'encoder lorsque celui-ci est tourné
void doEncoder() {
  if (digitalRead(encoder0PinA) == HIGH && digitalRead(encoder0PinB) == HIGH) {
    encoder_pos--;
  } else if (digitalRead(encoder0PinA) == HIGH && digitalRead(encoder0PinB) == LOW) {
    encoder_pos++;
  }
}

//Règle le potentiomètre digital à la position voulue et renvoi la valeur de résistance correspondante
float setPotWiper(int addr, int pos) {
  pos = constrain(pos, 0, 255);
  digitalWrite(csPin, LOW);
  SPI.transfer(addr);
  SPI.transfer(pos);
  digitalWrite(csPin, HIGH);

  return ((rAB * pos) / maxPositions) + rWiper;
}

//Permet d'afficher du texte sur l'écran OLED en précisant sa taille et sa position
void affichage_texte_OLED(String txt, int size, int c1, int c2) {
  ecranOLED.setTextSize(size);
  ecranOLED.setCursor(c1, c2);
  ecranOLED.setTextColor(SSD1306_WHITE);
  ecranOLED.print(txt);
}

//Permet d'afficher un entier sur l'écran OLED en précisant sa taille et sa position
void affichage_int_OLED(int value, int size, int c1, int c2) {
  ecranOLED.setTextSize(size);
  ecranOLED.setCursor(c1, c2);
  ecranOLED.setTextColor(SSD1306_WHITE);
  ecranOLED.print(value);
}

//Gère l'écran de bienvenue du banc de test
void welcome() {
  ecranOLED.clearDisplay();
  affichage_texte_OLED("BIENVENUE!", 2, 8, 26);
  ecranOLED.display();
  in_menu = false;
}

//Permet de configurer le mode d'utilisation du banc de test : flex sensor ou capteur graphite
void configuration() {
  if (in_menu) {
    encoder_pos = utiliser_graphite;
    while (in_menu) {
      menu();
      ecranOLED.clearDisplay();
      ecranOLED.setTextSize(2);
      ecranOLED.setCursor(0, 0);
      if (utiliser_graphite == 1) {
        ecranOLED.setTextColor(SSD1306_BLACK, SSD1306_WHITE);
        ecranOLED.println("Graphite");
        ecranOLED.setTextColor(SSD1306_WHITE, SSD1306_BLACK);
        ecranOLED.print("Flexsensor");
      } else {
        ecranOLED.setTextColor(SSD1306_WHITE, SSD1306_BLACK);
        ecranOLED.println("Graphite");
        ecranOLED.setTextColor(SSD1306_BLACK, SSD1306_WHITE);
        ecranOLED.print("Flexsensor");
      }
      ecranOLED.display();
      if (encoder_pos < 0) {
        encoder_pos = 0;
      } else if (encoder_pos > 1) {
        encoder_pos = 1;
      }
      utiliser_graphite = encoder_pos;
    }
    encoder_pos = 1;

  } else {
    ecranOLED.clearDisplay();
    affichage_texte_OLED("CONFIGURER", 2, 4, 26);
    ecranOLED.display();
  }
}

//Permet de calibrer le potentiomètre digital pour optimiser le signal si le capteur graphite est utilisé
void calibration() {

  if (in_menu) {
    for (int pos = pos_servo; pos > 0; pos -= 1) {
      myservo.write(pos);
      delay(15);
    }
    encoder_pos = R2_pos;

    while (in_menu) {
      menu();
      ecranOLED.clearDisplay();
      ecranOLED.setTextSize(2);
      ecranOLED.setCursor(0, 0);
      ecranOLED.setTextColor(SSD1306_WHITE);
      ecranOLED.print("VALEUR R2:");
      ecranOLED.println(res_pot);
      //ecranOLED.println(" ohms");
      ecranOLED.println("GRAPHITE:");
      ecranOLED.println(analogRead(graphite));
      ecranOLED.display();

      if ((encoder_pos > 0) && (encoder_pos <= 255)) {
        res_pot = setPotWiper(pot0, encoder_pos);
      } else if (encoder_pos > 255) {
        encoder_pos = 255;
      } else {
        encoder_pos = 0;
      }
      delay(100);
    }
    for (int pos = 0; pos < pos_servo; pos += 1) {
      myservo.write(pos);
      delay(15);
    }
    R2_pos = encoder_pos;
    encoder_pos = 2;
  } else {
    ecranOLED.clearDisplay();
    affichage_texte_OLED("CALIBRER", 2, 20, 26);
    ecranOLED.display();
  }
}

//Permet de régler la vitesse de fonctionnement du servo moteur durant les tests
void vitesse() {
  if (in_menu) {
    encoder_pos = val_vit;
    for (int pos = pos_servo; pos < 180; pos += 1) {
      myservo.write(pos);
      delay(val_vit);
    }

    while (in_menu) {
      menu();
      ecranOLED.clearDisplay();
      ecranOLED.setTextSize(2);
      ecranOLED.setCursor(0, 0);
      ecranOLED.setTextColor(SSD1306_WHITE);
      ecranOLED.println("Vitesse:");
      ecranOLED.print(round(val_vit * (-2.84) + 114.3));
      ecranOLED.print("%");
      ecranOLED.display();

      if (encoder_pos < 5) {
        encoder_pos = 5;
      } else if (encoder_pos > 40) {
        encoder_pos = 40;
      }

      if (val_vit != encoder_pos) {
        for (int pos = 180; pos > 0; pos -= 1) {
          if ((encoder_pos >= 5) && (encoder_pos <= 40)) {
            myservo.write(pos);
            delay(encoder_pos);
          } else if (encoder_pos < 5) {
            encoder_pos = 5;
            myservo.write(pos);
            delay(encoder_pos);
          } else {
            encoder_pos = 40;
            myservo.write(pos);
            delay(encoder_pos);
          }
        }
        for (int pos = 0; pos < 180; pos += 1) {
          if ((encoder_pos >= 5) && (encoder_pos <= 40)) {
            myservo.write(pos);
            delay(encoder_pos);
          } else if (encoder_pos < 5) {
            encoder_pos = 5;
            myservo.write(pos);
            delay(encoder_pos);
          } else {
            encoder_pos = 40;
            myservo.write(pos);
            delay(encoder_pos);
          }
        }
        val_vit = encoder_pos;
      }
      delay(100);
    }
    val_vit = encoder_pos;
    encoder_pos = 3;
    for (int pos = 180; pos > pos_servo; pos -= 1) {
      myservo.write(pos);
      delay(val_vit);
    }
  } else {
    ecranOLED.clearDisplay();
    affichage_texte_OLED("VITESSE", 2, 22, 26);
    ecranOLED.display();
  }
}

//Permet de régler la borne de fin de course du servo pour ne pas endommager l'extrémité d'un capteur
void borne() {
  if (in_menu) {
    encoder_pos = pos_servo;
    while (in_menu) {
      menu();
      ecranOLED.clearDisplay();
      ecranOLED.setTextSize(2);
      ecranOLED.setCursor(0, 0);
      ecranOLED.setTextColor(SSD1306_WHITE);
      ecranOLED.println("Borne sup:");
      ecranOLED.print(encoder_pos);
      ecranOLED.display();
      if ((encoder_pos > 0) && (encoder_pos <= 180)) {
        myservo.write(encoder_pos);
        delay(15);
      } else if (encoder_pos > 180) {
        encoder_pos = 180;
      } else {
        encoder_pos = 0;
      }
      delay(100);
    }
    pos_servo = encoder_pos;
    valeur_borne = encoder_pos;
    encoder_pos = 4;
  } else {
    ecranOLED.clearDisplay();
    affichage_texte_OLED("BORNE", 2, 38, 26);
    ecranOLED.display();
  }
}

//Permet à l'utilisateur de définir le nombre de mesures sur lesquelles la moyenne de la résistance sera calculée
void mode_mesure() {

  if (in_menu) {

    encoder_pos = nmbre_repet;

    while (in_menu) {
      menu();
      ecranOLED.clearDisplay();
      ecranOLED.setTextSize(2);
      ecranOLED.setCursor(0, 0);
      ecranOLED.setTextColor(SSD1306_WHITE);
      ecranOLED.print("Nbr repet:");
      ecranOLED.print(nmbre_repet);
      ecranOLED.display();

      if ((encoder_pos >= 1) && (encoder_pos <= 20)) {
        nmbre_repet = encoder_pos;
      } else if (encoder_pos < 1) {
        encoder_pos = 1;
      } else {
        encoder_pos = 20;
      }
    }
    nmbre_repet = encoder_pos;
    encoder_pos = 5;

  } else {
    ecranOLED.clearDisplay();
    affichage_texte_OLED("   MODE", 2, 5, 19);
    affichage_texte_OLED("  MESURE", 2, 5, 34);
    ecranOLED.display();
  }
}

//Permet de démarrer une mesure puis d'afficher la moyenne obtenue
void lancer_mesure() {

  if (in_menu) {
    Valeur_graphite = 0;
    Valeur_flex = 0;
    for (int i = pos_servo; i > 0; i--) {
      myservo.write(i);
      delay(val_vit);
    }

    for (int j = 1; j <= nmbre_repet; j++) {
      ecranOLED.clearDisplay();
      ecranOLED.setTextSize(2);
      ecranOLED.setCursor(0, 0);
      ecranOLED.setTextColor(SSD1306_WHITE);
      ecranOLED.print("Essai ");
      ecranOLED.println(j);
      ecranOLED.print("en cours:");
      ecranOLED.display();
      for (int i = 0; i < valeur_borne; i++) {

        myservo.write(i);
        delay(val_vit);
      }
      delay(1000);

      if (utiliser_graphite == 1) {
        Valeur_graphite += analogRead(graphite);
      } else {
        Valeur_flex += analogRead(flexPin);
      }
      for (int k = valeur_borne; k >= 0; k--) {
        myservo.write(k);
        delay(val_vit);
      }
      delay(1000);
    }

    if (utiliser_graphite == 1) {
      Valeur_graphite = Valeur_graphite / nmbre_repet;
      V_value_graph = Valeur_graphite * (VCC / 1023.0);
      resistance = ((1 + (R3 / res_pot)) * (VCC / V_value_graph)) * R1 - R1 - R5;

      ecranOLED.clearDisplay();
      ecranOLED.setTextSize(2);
      ecranOLED.setCursor(0, 0);
      ecranOLED.setTextColor(SSD1306_WHITE);
      ecranOLED.println("Resistance");
      ecranOLED.print(resistance);
      ecranOLED.display();
      delay(20);


    } else {
      Valeur_flex = Valeur_flex / nmbre_repet;
      V_value = Valeur_flex * VCC / 1023.0;
      R_value = R * V_value / (VCC - V_value);
      angle = map(R_value, flatR, bendR, 0.0, 90.0);

      ecranOLED.clearDisplay();
      ecranOLED.setTextSize(2);
      ecranOLED.setCursor(0, 0);
      ecranOLED.setTextColor(SSD1306_WHITE);
      ecranOLED.println("Resistance");
      ecranOLED.println(R_value);
      ecranOLED.println("Angle");
      ecranOLED.print(angle);
      ecranOLED.display();
      delay(20);
    }
    for (int i = 0; i < pos_servo; i++) {
      myservo.write(i);
      delay(val_vit);
    }
    delay(10000);
    in_menu = false;

  } else {
    ecranOLED.clearDisplay();
    affichage_texte_OLED("DEMARRAGE", 2, 12, 26);
    ecranOLED.display();
  }
}
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

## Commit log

2025-04-20 Changement de nom
2025-05-20 Create PCB_design

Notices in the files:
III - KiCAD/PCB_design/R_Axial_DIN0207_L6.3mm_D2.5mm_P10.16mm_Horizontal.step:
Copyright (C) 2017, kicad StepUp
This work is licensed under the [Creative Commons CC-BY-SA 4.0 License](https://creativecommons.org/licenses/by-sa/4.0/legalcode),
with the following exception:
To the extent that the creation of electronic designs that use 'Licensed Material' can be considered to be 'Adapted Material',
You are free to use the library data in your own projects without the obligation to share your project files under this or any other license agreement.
